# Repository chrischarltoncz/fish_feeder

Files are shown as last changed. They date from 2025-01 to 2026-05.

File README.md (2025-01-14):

# fish_feeder



This is the python code to run the pneumatic fish feeder system which functions as follows:

The food is placed in a clear plastic cylinder/hopper. There is an illumination LED strip to light it up on one side. A Pi camera on the opposite side to capture images of the tube and the food. This image will be used for tracking food consumption and level.

The base of the tube has the main feeder body, this incorporates a delrin screw drive to move the food. The screw is rotated via at NEMA17 motor at one end, at the opposite end is an opto sensor and a 6 slot chopper for counting the rotations. This is used to confirm the rotation happens and the motor is not jammed.

The thread deposits the food into a conical volume, this funnels it down to a fitting where it exits the food hopper body/assembly. Above the conical volume is mounted an air solenoid valve, it is fed via 22-25psi house air. The air supply is split off via a needle valve to supply a small continuous stream of air that travels to the bulk food.
This is to keep it dry, it also passes over a temperature and humidity sensor to record the values, this ensures the food is always exposed to dry air and if there is an air supply problem it can be flagged.

Currently (Jan 2025) the air solenoid is turned on prior to the food loading screw rotation, this is to equalize the pressure along the various parts (thread/hopper) so fine powdered food does not flow and collect/jam the screw mech.

Once the food passes out of the food hopper mech, it passes to the rotary valve mechanism.

There is a curved interface tube which is centrally located and passes to near the circumference of a rotating disc, this disc has embedded magnets which lightly clamp the rotor to the stator, the stator underneath has 30X fittings which correspond to each fish tank. 

The rotor is turned via a belt which is in turn rotated via a NEMA23 stepper motor. A home sensor microswitch is stationary on the main feeder assembly, it activates via a 3D printed bump which is VHB taped to the rotor. There is a well defined number of microsteps between home and port 1 so the system can home and index to the correct port location.

One each feeding cycle the rotor is re-homed, then indexed to port 1. Prior to food loading the tank/port is air dried for a number of seconds (typically 60-75) to dry the end of the tube to avoid wet food. 

Links:

Stepper motor drive boards:
https://www.allmotion.com/ezhr17en

Onshape design:
[https://www.allmotion.com/ezhr17en
](https://cad.onshape.com/documents/b092e7b6adc17bd3a3390fe1/w/5d2cf434299dfa3fc55c8225/e/223d4cf3e3f1612e807b6f1d?renderMode=0&uiState=6785ac46c4b3921eef4992e4)

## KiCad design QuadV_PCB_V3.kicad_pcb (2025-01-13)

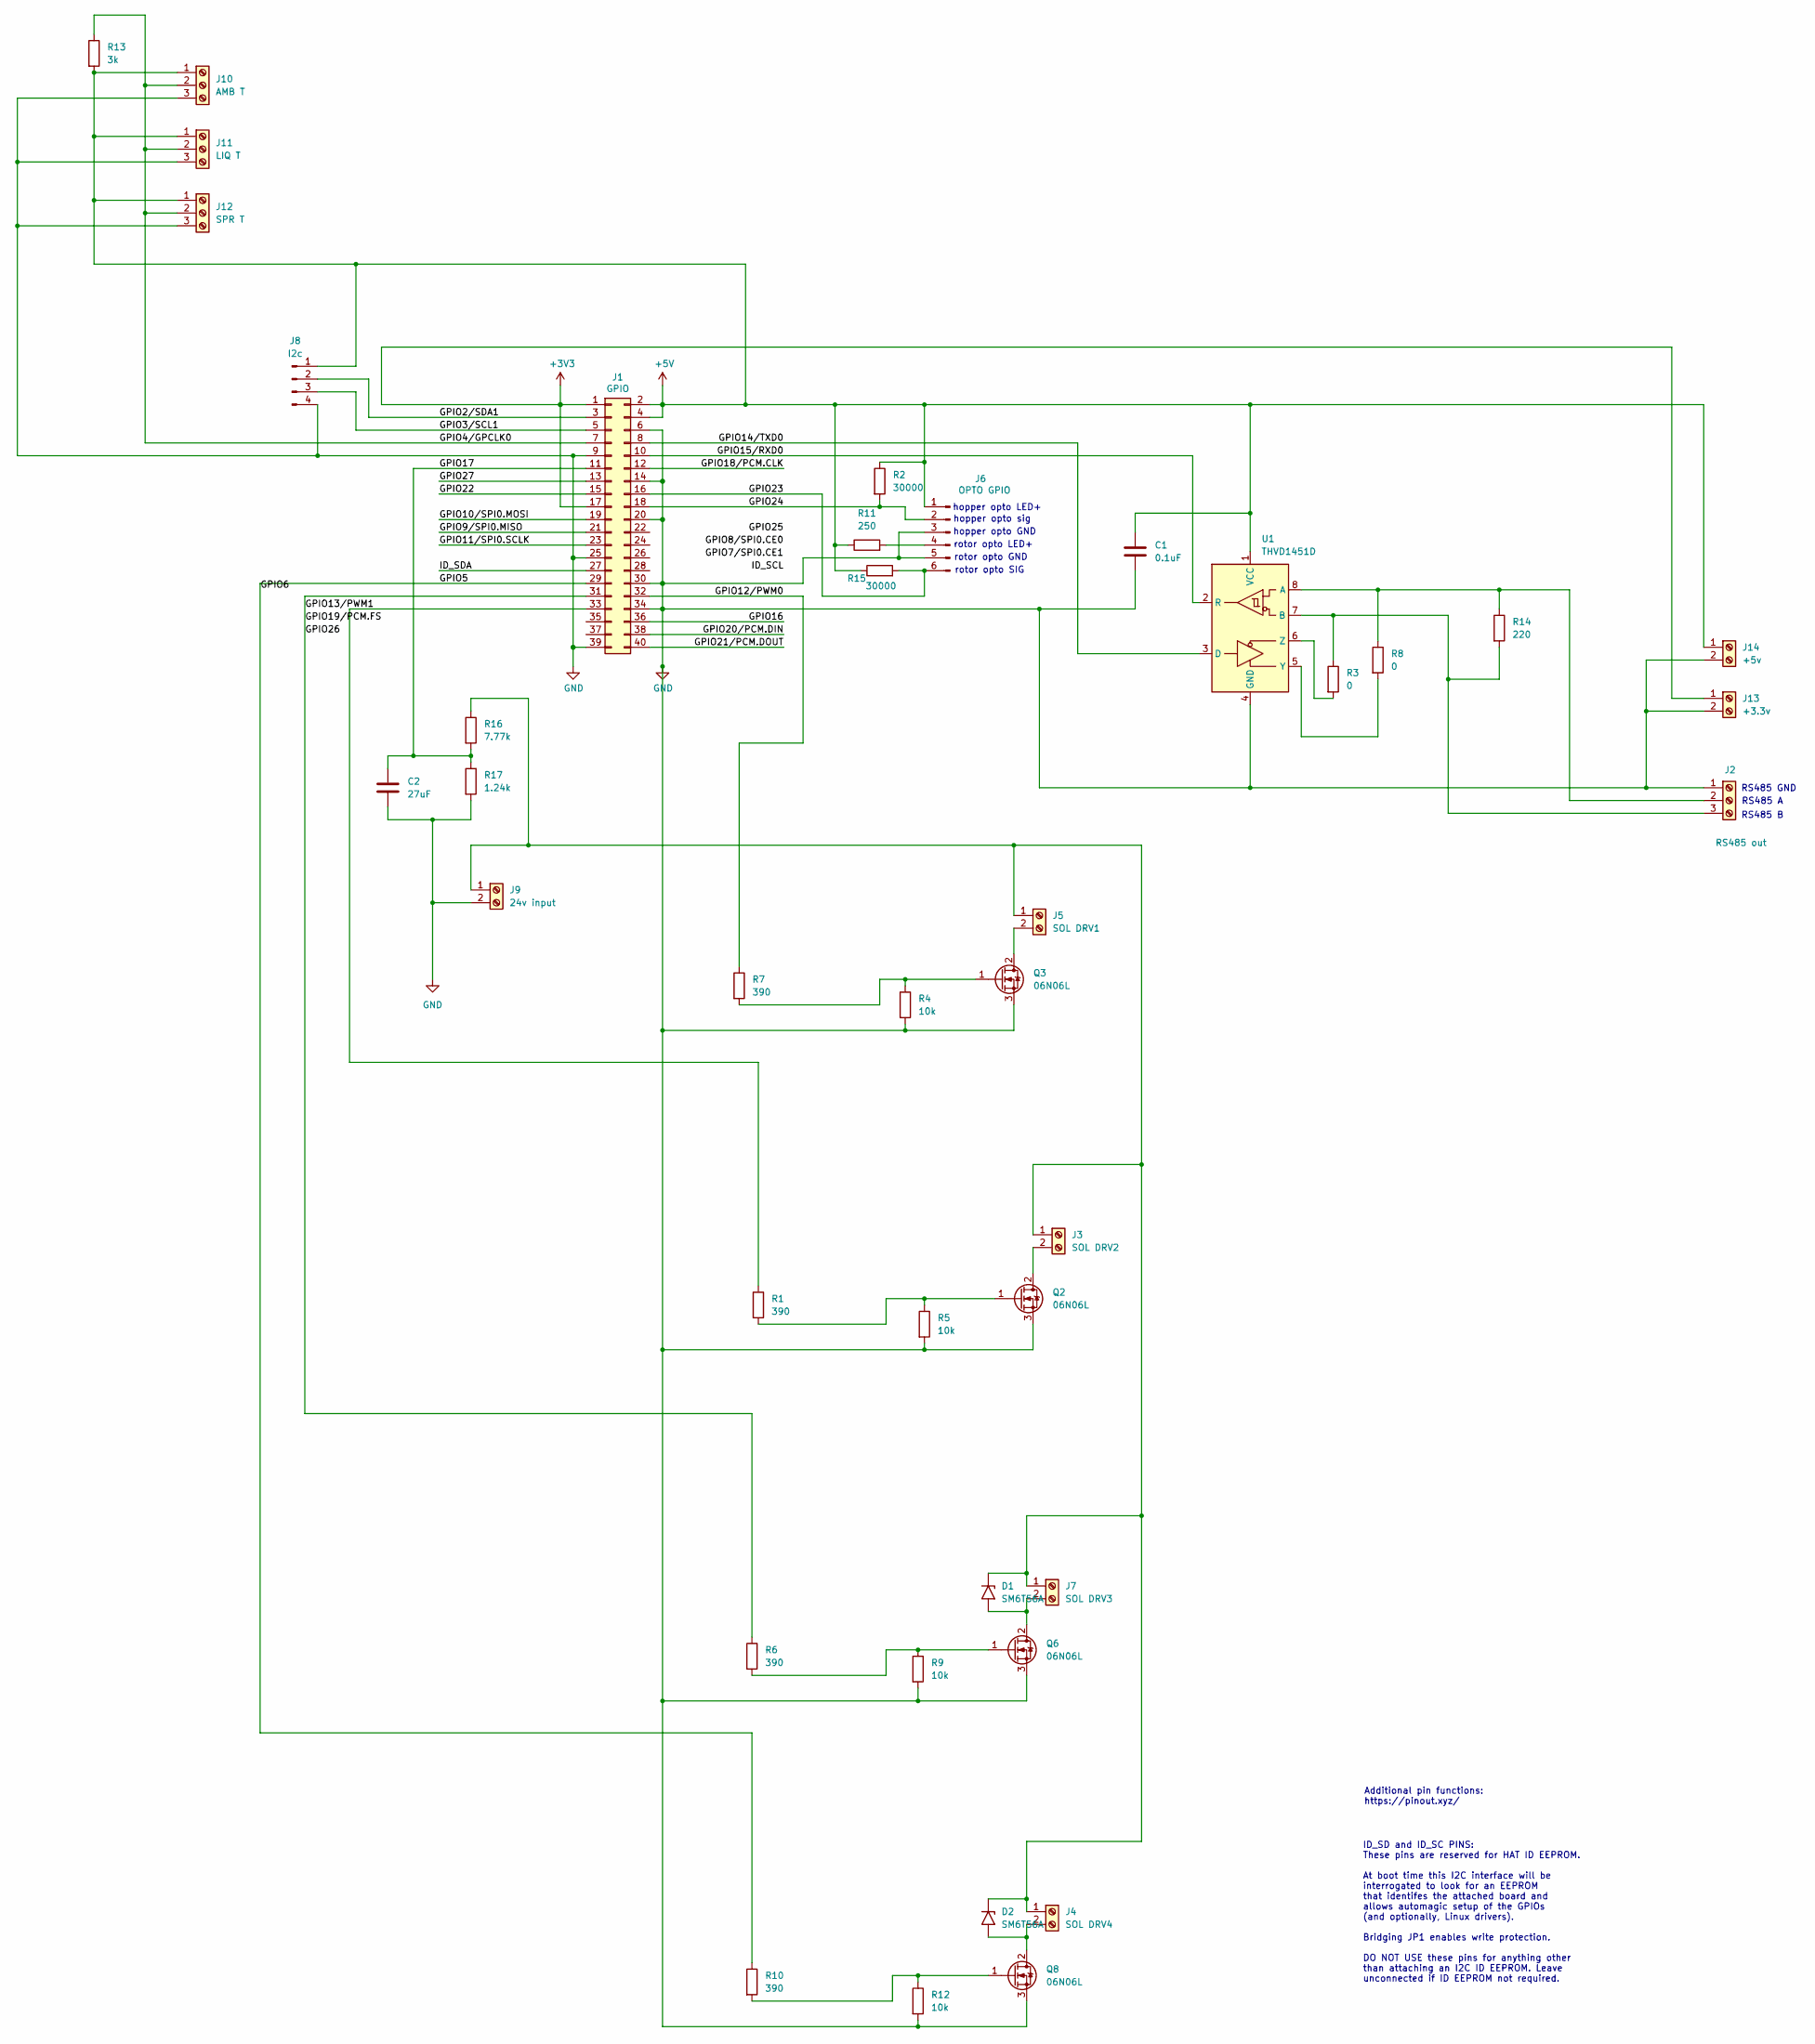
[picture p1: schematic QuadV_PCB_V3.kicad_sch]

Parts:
C1: 0.1uF; C_0201_0603Metric
C2: 27uF; CP_Elec_6.3x5.9
D1, D2: SM6T56A; D_SMB
J1: GPIO; PinSocket_2x20_P2.54mm_Vertical
J2: RS485 out; TerminalBlock_Xinya_XY308-2.54-3P_1x03_P2.54mm_Horizontal
J3: SOL DRV2; TerminalBlock_bornier-2_P5.08mm
J4: SOL DRV4; TerminalBlock_bornier-2_P5.08mm
J5: SOL DRV1; TerminalBlock_bornier-2_P5.08mm
J6: OPTO GPIO; Molex_KK-254_AE-6410-06A_1x06_P2.54mm_Vertical
J7: SOL DRV3; TerminalBlock_bornier-2_P5.08mm
J8: I2c; Molex_KK-254_AE-6410-04A_1x04_P2.54mm_Vertical
J9: 24v input; TerminalBlock_Phoenix_MKDS-1,5-2-5.08_1x02_P5.08mm_Horizont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
J10: AMB T; TerminalBlock_Xinya_XY308-2.54-3P_1x03_P2.54mm_Horizontal
J11: LIQ T; TerminalBlock_Xinya_XY308-2.54-3P_1x03_P2.54mm_Horizontal
J12: SPR T; TerminalBlock_Xinya_XY308-2.54-3P_1x03_P2.54mm_Horizontal
J13: +3.3v; TerminalBlock_Xinya_XY308-2.54-2P_1x02_P2.54mm_Horizontal
J14: +5v; TerminalBlock_Xinya_XY308-2.54-2P_1x02_P2.54mm_Horizontal
Q2, Q3, Q6, Q8: 06N06L; SOT-23-3
R1, R6, R7, R10: 390; R_0603_1608Metric
R2, R15: 30000; R_0603_1608Metric
R3, R8: 0; R_0603_1608Metric
R4, R5, R9, R12: 10k; R_0603_1608Metric
R11: 250; R_0603_1608Metric
R13: 3k; R_0603_1608Metric
R14: 220; R_0603_1608Metric
R16: 7.77k; R_0603_1608Metric
R17: 1.24k; R_0603_1608Metric
U1: THVD1451D; SOIC-8_3.9x4.9mm_P1.27mm

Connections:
+3V3: J1.1, J1.17, J13.1
+5V: C1.1, J1.2, J1.4, J6.1, J8.1, J10.1, J11.1, J12.1, J14.1, R2.1, R11.1, R13.2, R15.1, U1.1 (VCC)
/GPIO2/SDA1: J1.3, J8.2
/GPIO3/SCL1: J1.5, J8.3
/GPIO4/GPCLK0: J1.7, J10.2, J11.2, J12.2, R13.1
/GPIO5: J1.29, R10.1
/GPIO9/SPI0.MISO: J1.21
/GPIO10/SPI0.MOSI: J1.19
/GPIO11/SPI0.SCLK: J1.23
/GPIO12/PWM0: J1.32, R7.1
/GPIO13/PWM1: J1.31, R6.1
/GPIO14/TXD0: J1.8, U1.3 (D)
/GPIO15/RXD0: J1.10, U1.2 (R)
/GPIO16: J1.36
/GPIO17: C2.1, J1.11, R16.2, R17.1
/GPIO18/PCM.CLK: J1.12
/GPIO20/PCM.DIN: J1.38
/GPIO21/PCM.DOUT: J1.40
/GPIO22: J1.15
/GPIO23: J1.16, J6.6, R15.2
/GPIO24: J1.18, J6.2, R2.2
/GPIO27: J1.13
/ID_SDA: J1.27
GND: C1.2, C2.2, J1.6, J1.9, J1.14, J1.20, J1.25, J1.30, J1.34, J1.39, J2.1, J6.3, J6.5, J8.4, J9.2, J10.3, J11.3, J12.3, J13.2, J14.2, Q2.3 (S), Q3.3 (S), Q6.3 (S), Q8.3 (S), R4.2, R5.2, R9.2, R12.2, R17.2, U1.4 (GND)
unnamed: D1.1 (A1), D2.1 (A1), J3.1, J4.1, J5.1, J7.1, J9.1, R16.1
unnamed: D1.2 (A2), J7.2, Q6.2 (D)
unnamed: D2.2 (A2), J4.2, Q8.2 (D)
unnamed: J1.33, R1.1
unnamed: J2.2, R8.1, R14.1, U1.8 (A)
unnamed: J2.3, R3.1, R14.2, U1.7 (B)
unnamed: J3.2, Q2.2 (D)
unnamed: J5.2, Q3.2 (D)
unnamed: J6.4, R11.2
unnamed: Q2.1 (G), R1.2, R5.1
unnamed: Q3.1 (G), R4.1, R7.2
unnamed: Q6.1 (G), R6.2, R9.1
unnamed: Q8.1 (G), R10.2, R12.1
unnamed: R8.2, U1.5 (Y)
unnamed: R3.2, U1.6 (Z)

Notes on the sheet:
Additional pin functions: https://pinout.xyz/
hopper opto GND
RS485 GND
RS485 A
ID_SD and ID_SC PINS: These pins are reserved for HAT ID EEPROM. At boot time this I2C interface will be interrogated to look for an EEPROM that identifes the attached board and allows automagic setup of the GPIOs (and optionally, Linux drivers). Bridging JP1 enables write protection. DO NOT USE th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
RS485 B
rotor opto LED+
rotor opto SIG
hopper opto sig
hopper opto LED+
rotor opto GND

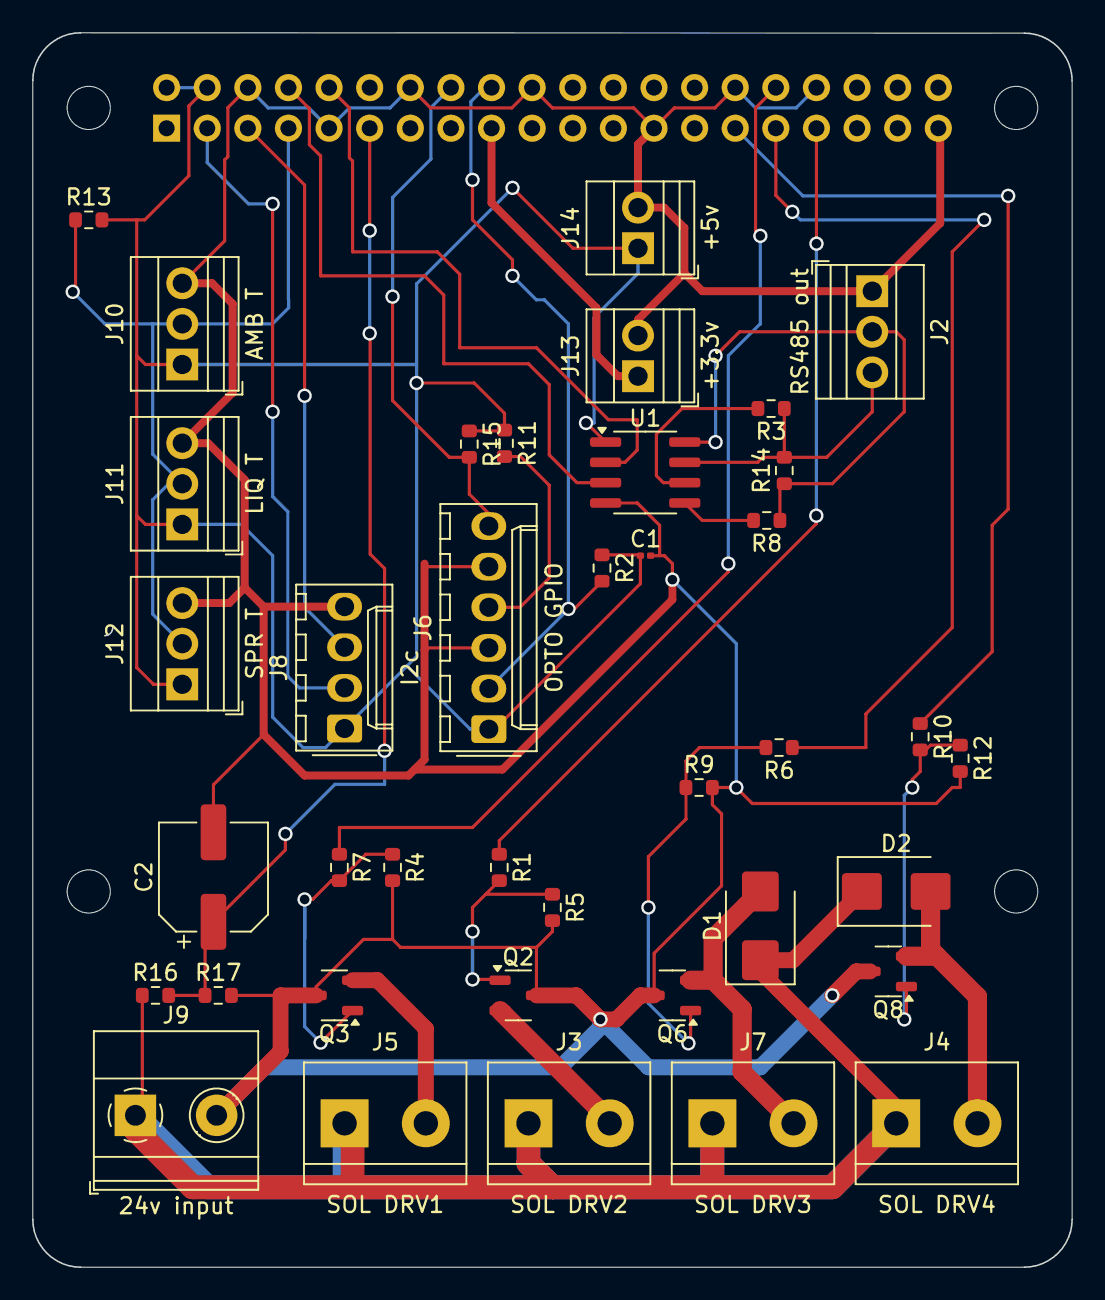
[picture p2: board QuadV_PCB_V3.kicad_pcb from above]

Board: 2 copper layers, 65.0 x 77.2 mm, 44 parts (1 on the bottom side), 29 nets.

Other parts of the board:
MH1, MH2, MH3, MH4: MountingHole_2.7mm_M2.5

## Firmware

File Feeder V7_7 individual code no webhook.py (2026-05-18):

# ==============================================================================
# Fish Feeding System - Individual Feeder Pi
# Version: v7.7
# Description: Web interface and control system for individual fish feeder
#              stations running on Raspberry Pi 4
# ==============================================================================
#
# Change LOG:
# V2.0 - started adding in physical control functions
# V2.1 - added manual home button to run the control functions manually
# V2.2 - added more buttons with value inputs on the required functions
# V2.3 - camera fix
# V2.4 - another camera fix
# V2.5 - another camera fix plus added LED function
# V2.6 - global port value tracked
# V2.7/2.8 ??
# V2.9 - adjusted the values to find the food level correctly
# V3.0 - claude attempted to repair the hopper feed and counting opto functions
# V3.1 - manual control page changes
# V3.2 - status on manual control page
# V3.3 - fixed manual control page buttons unresponsive (JS newline escape bug in activity log)
# V3.4 - moved Settle motor button under Load Food, added value input (1-20) passed to SettleMotor
# V3.5 - SettleMotor name conflict resolved (SettleMotorState), home page port fix, camera buffer flush fix, Slack test button
# V4.0 - full code review pass: bug fixes (BlowAirLong GPIO.state, CleanRotor undefined `times`, JiggleRotor int+str concat, broken MQTT initFeeder calls), CheckFoodLevel now actually runs analysis, MovePorts validates start position, exception handling hardened across module-level init / serial / sensor / Slack / threads / main(), API routes refactored with hw_action decorator, _serial_write helper, GPIO.cleanup on exit, sys.excepthook installed, load_webhook reads from sidecar file, home page auto-refreshes, current_port globals consolidated
# V4.1 - removed Microsteps/Turns-per-mg fields from config page, added MICROSTEPS_TO_PORT_ONE constant (replaces hardcoded 4400 in MoveToPortOne), home page heading now shows version
# V4.2 - added Temp Hum log page (Chart.js dual-axis plot), hourly temp/humidity logger to CSV, 5-day rolling retention, pre-seed defaults (22C / 40%) on first boot
# V4.3 - Temp Hum plot now shows last 24 h only (rolling 24 data points); CSV file still stores 5 days for history
# V4.4 - camera preview image scaled to 600x451 in the browser (preserves 1640x1232 aspect ratio); stream resolution unchanged
# V4.5 - added CheckClogs() reading GPIO 4, Check Clog button + Hopper Clogged status row on Manual Control page
# V4.6 - added CheckPower() reading GPIO 17, Check Power button + +24 volts ok status row on Manual Control page
# V4.7 - added CheckAir() reading GPIO 25 (function only, no UI elements)
# V4.8 - added RunFoodSequence() with pre-checks, per-tank feeding loop, post-clean and Slack notifications; skips feeding+clean when no tanks enabled, advances to first enabled tank if port 1 disabled
# V4.9 - RunFoodSequence now Slacks "Food remaining X %" before and after the feeding cycle (forces a fresh food-level read each time)
# V5.0 - added CheckFeedTiming daemon loop; fires RunFoodSequence on a schedule driven by "Feeds per 24 hours"; persists last-feed time across reboots; reads config live so UI changes take effect without restart
# V5.1 - version bump only
# V5.2 - added IdleTubeDry daemon (walks rotor port-by-port between feeds, gated by dry_enabled checkbox), 10-min pre-feed guard, mutual-exclusion lock with RunFoodSequence
# V5.3 - fixed home page "Next Scheduled Feeding" never updating (was hardcoded to "Not scheduled"); added _refresh_next_feeding_time() called from CheckFeedTiming tick and config save handler
# V5.4 - full code review pass: bug fixes (MovePorts off-by-one wrap, RunFoodSequence zero-port-move turning into 60-port spin, IdleTubeDry holding lock during X-min sleep blocking feeds), exception handling hardened (RunFoodSequence per-tank loop now guarantees air solenoid OFF on failure, threading.excepthook installed for daemon thread crashes, Slack send retries once on 5xx, SetupSystemBoot warns when serial port unavailable), concurrency (all hardware API routes acquire _feed_lock via hw_action decorator, MQTT initFeeder lock-wrapped, system_errors bounded at 200 entries), cleanup (dead code removed: WIFI creds, next_port_swap_time, runFoodSchedule stub; immediateFoodNow now actually delegates to RunFoodSequence; display_message renamed to report_crash; food_scale comment fixed; LightTube comment fixed; sidecar directories auto-created; food analysis loop dedupes repeat errors; "Cycle in progress" surfaced on home page; footer summary refreshed; typo "excepion"->"exception")
# V5.5 - fixed home page "Next Scheduled Feeding" sliding (in-memory fallback when last_feed.txt unreadable, removed silent `or datetime.now()` lying); CheckAir polarity corrected (sensor pulls LOW when air flowing — function now returns normalised True/False, all callers updated); current_port concurrency model documented
# V5.6 - inverted the air sensor polarity, it was incorrect
# V5.7 - fixed Immediate Feed silently overwriting the scheduled tank list (was writing form values to TankSettings); RunFoodSequence now takes tank_section parameter, immediateFoodNow writes to ImmediateFeed only
# V5.8 - added activity log textarea to home page (mirrors Manual Control page format), poller now logs "Status refreshed" / failures with timestamps
# V5.9 - home page activity log now shows real backend events (feed cycles, idle dry moves, manual actions, errors) instead of poll noise; new ring buffer + /api/recent_events endpoint, log_event() instrumentation across RunFoodSequence, CheckFeedTiming, IdleTubeDry, immediateFoodNow, hw_action; system_errors_append mirrors errors to the event log
# V6.0 - external port numbering normalised to 1-60 (with "HOME"/"UNKNOWN" labels for special states); new _display_port() helper applied to home page, manual page, /api/status, /api/manual_status and MQTT reqStat; Move ports input range fixed to 1-60 across label/input/JS validator/server validator (was a 3-way mismatch)
# V6.1 - added "Pre-food air dry time" dropdown (5-60s in 5s steps) to Fish Feeder Configuration page; RunFoodSequence now blasts air for the configured duration before each LoadFood to clear moisture from the dispense tube
# V6.2 - added per-tank free-text label input on Fish Feeder Configuration page (40-char max); persisted to TankSettings as tank_<n>_label; pre-populated from saved value on page reload
# V6.3 - RunFoodSequence now Slacks "Feeding tanks: 1,5,6,..." at cycle start and "Next feed scheduled for: <ts>" at cycle end
# V6.4 - per-tank label input moved onto its own row below checkbox/food/mg on Configuration page (was cramped horizontally per attached screenshot); same restructure on Immediate Feed page; new .tank-item-row CSS class
# V6.5 - new "Only dry active tubes" checkbox on Configuration page; when enabled, IdleTubeDry walks only the enabled-tank ports (read fresh from TankSettings on each iteration) instead of every port 1..60; if currently parked on a disabled port, daemon repositions before the next dry wait rather than wasting a cycle
# V6.6 - send Slack notification at startup announcing system online + software version
# V6.7 - food-level calibration overhaul: ROI widened from (120..1340) to (0..1500), vertical extent tightened from 360 px to 180 px (snapshot space) by shifting each y edge inward by 90 snapshot px (y1 500->545, y2 680->635); FOOD_FULL_X = 1446 (right end, where food sits when tube is full), FOOD_EMPTY_X = 0 (left end, where food has receded to when consumed). Earlier in v6.7 these were assigned the wrong way round and a clearly ~60% full tube read 0.76% — the swap brought the reading back in line with reality (~61%)
# V6.8 - revision bump only; v6.7's food-level calibration verified against a known ~60%-full tube (reads ~61%, matches visual estimate)
# V6.9 - food-level percentage rounded to nearest 0.5% via new _round_food_pct() helper applied at all display/notification sites (home page, /api/status, MQTT status, pre/post Slack lines, log_event); RunFoodSequence now Slacks "Food consumed this feeding: X %" at the end of each cycle (pre minus post, clamped to 0 to absorb camera noise; volatile, not persisted)
# V7.0 - RunFoodSequence now also Slacks two derived metrics after each cycle: "% food used per gram" (consumed % divided by total mg dispensed, converted to g) and "No. of feedings left in the feeder" (current remaining % divided by this cycle's consumed %, rounded down). Both volatile, not persisted; computed only when a non-zero consumed delta is available
# V7.1 - RunFoodSequence now collects food_ratio (actual hopper turns / theoretical turns, set by LoadFood) after each per-tank dispense and Slacks the per-cycle mean as "Average hopper food turn ratio" at the end. 1.0 is ideal; lower indicates jamming/slip. Volatile, not persisted.
# V7.2 - scheduling overhauled: legacy "Feeds per 24 hours" interval scheduler replaced with up-to-10 fixed-time daily feed slots set on a new "Feeding times per 24 hour" page (accessed from a button next to Save Configuration / Home Rotor). Strict semantics — a slot whose moment passes while the system is offline is skipped, not caught up. CheckFeedTiming, _minutes_to_next_feed, _refresh_next_feeding_time, post-cycle "Next feed scheduled for" Slack message all rewired to consult _next_scheduled_feed_datetime() instead of the interval math. Legacy feeds_per_24_hours config key left in feeder_config.ini for backwards-compat but no longer consulted.
# V7.3 - UI polish: removed "Home Rotor" button (and its orphaned homeRotor() JS handler) from the bottom of the Configuration page; recoloured the "Temp Hum log" button on the home page from blue/btn-primary to a new dark-mustard btn-temp class so it's visually distinct from the other primary buttons.
# V7.4 - Manual Control page button recolouring: new btn-warning class (orange) for Food Light and Load Food; everything else recoloured per user spec — Home Rotor/Move to Port One/Check food level/Check Clog/Check Power/Slack test/Move ports/Blow Air/Clean Rotor/Settle motor all green (btn-success); Setup allmotion stays grey (btn-secondary).
# V7.5 - removed the never-wired "Regular Feed Schedule" and "Delay Feed by Normal Amount" checkboxes from the Immediate Feed page; cleaned up the matching form reads, config writes, default keys, helper function signature, and the JS handler that gave them mutual-exclusivity behaviour. The .ini keys are no longer written for new configs (existing .inis keep the stale keys harmlessly — they're just orphaned).
# V7.6 - Immediate Feed page now always renders the per-tank label slot (read-only, sourced from TankSettings as before); tanks with no label saved show "N/A" instead of being silently hidden, so the user can see at a glance which tanks have been named.
# V7.7 - home page "Next Scheduled Feeding" tile now uses the same time-on-top / date-below format as the upper clock: 12-hour time with AM/PM rendered bold on the first line, DD:MM (no year) on a smaller line beneath. next_feeding_time now emits the two parts joined with '\n'; home template + JS poller both split on the newline. New .value-sub CSS class added for the date line.


import serial
import os
import io
import time
import board
import adafruit_ahtx0
import RPi.GPIO as GPIO
import datetime
import threading
import configparser
import collections
import cv2
import numpy as np
from datetime import datetime, timedelta
from flask import Flask, render_template_string, request, redirect, url_for, jsonify, Response
import paho.mqtt.client as mqtt

# for slack notifications:
import requests
# for exception crash handling
import sys
import traceback
import atexit
# decorator support for the API hardware-action wrapper
import functools
# imported once at module level (was previously imported inside several camera functions)
from PIL import Image
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

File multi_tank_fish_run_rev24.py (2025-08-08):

# Chris C. 6th AUG 2025

# Rev12 incorporates the camera to grab an image of the feed tube per feeding cycle (4 images per day)
# Rev13 the feed screw was jamming after 50 cycles. Rev13 has new hardware but also turns on the air prior to the feed screw turn
# this should clear fine powdered food from the end of the screw
# calibration went from 20 to 22.5 for 125mg
# Rev14 added 3X gearing to the hopper mech
# this requires V600 speed instead of V200 to account for the gearing
# it also requires reversal of the motor direction because the gear changes it
# Rev16 added function to feed specific tanks for manual use
# Rev19 works 25 tanks
# Rev20 added text file import to define food amounts per tank
# Rev21 added a slack notification to a feeder channel
# Rev22 adjusted the loop timer for hopper loading. Added extra loop time and adjusted the loop delay from 0.02 to 0.01 seconds. Also added a while loop if the state is TRUE when the timer starts wait for it to go FALSE before looping/counting
# added global exception handler to send slack if the code crashes anytime
# this should be fixed: fix the hopper screw slot count, it still counts wrong sometimes (6.22?) should be 0.99 to 1 normally
# Rev23 report the hopper screw ratio in slack, the minimum ratio during the whole feeding cycle. Can now have zero values in the food quantity text file and it will just skip those and send no food
# Rev24 if there is less than 5 mins to go before a feed cycle the rotor won't rotate to do the tank tube drying, this is so it doesn't interfere with the feeding cycle


# THINGS TO IMPROVE:
# slow down the hopper screw speed, doesnt need to be that quick
# optimize some of the wait times to speed up the total feeding time
# slack out the food level % or equivalent. Send notification at the start of the feed cycle and afterwards. So it can be determined that its dropping
# fix the hopper screw slot count, it still counts wrong sometimes (6.22?) should be 0.99 to 1 normally. DONE?
# check the auto dry rotation doesn't interfere with the feeding cycle right when the feeding starts. DONE? if less than 5 mins to go won't turn rotor
# add a feature to allow the food file to have zero's in it if a tank needs to be skipped. DONE?
# calibrate the food dispense and make sure its correct



# general imports:
import serial
import time
import board
import adafruit_ahtx0
import RPi.GPIO as GPIO
import datetime
from picamera2 import Picamera2

# for loading food quantities
import ast
from typing import Dict, Tuple

# for slack notifications:
import requests

# for exception crash handling
import sys
import traceback

# GPIO
GPIO.setup(24, GPIO.IN) # this is the hopper opto thread sensor input

# UART port definition 
port = "/dev/ttyAMA0"
baud = 9600
# UART port:
ser = serial.Serial("/dev/serial0", baudrate=9600, timeout=2.0)
    # open the serial port
if ser.isOpen():
    print(ser.name + ' is open...')

# Temp/Hum sensor AHT
sensor = adafruit_ahtx0.AHTx0(board.I2C())
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

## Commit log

2025-01-13 Add files via upload
    Fish feeder and quadravision PCB KiCAD files Version 3 (jan 2025)
    [QuadV_PCB_V3.kicad_pcb, QuadV_PCB_V3.kicad_sch]
2025-01-14 Add files via upload
    Capture image using Pi camera, output a level based off the image of food
2025-01-30 This version has the changes for the 3:1 gears
    3:1 gearbox scale changes and motor speeds, also extension to 30 days for a longer test
2025-08-08 Add files via upload
    # Rev22 adjusted the loop timer for hopper loading. Added extra loop time and adjusted the loop delay from 0.02 to 0.01 seconds. Also added a while loop if the state is TRUE when the timer starts wai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
    # added global exception handler to send slack if the code crashes anytime
    # this should be fixed: fix the hopper screw slot count, it still counts wrong sometimes (6.22?) should be 0.99 to 1 normally
    # Rev23 report the hopper screw ratio in slack, the minimum ratio during the whole feeding cycle. Can now have zero values in the food quantity text file and it will just skip those and send no food
    # Rev24 if there is less than 5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
